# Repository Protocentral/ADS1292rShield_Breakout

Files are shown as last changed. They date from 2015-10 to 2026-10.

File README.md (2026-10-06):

ProtoCentral ADS1292R ECG/respiration shield and breakout board 
================================

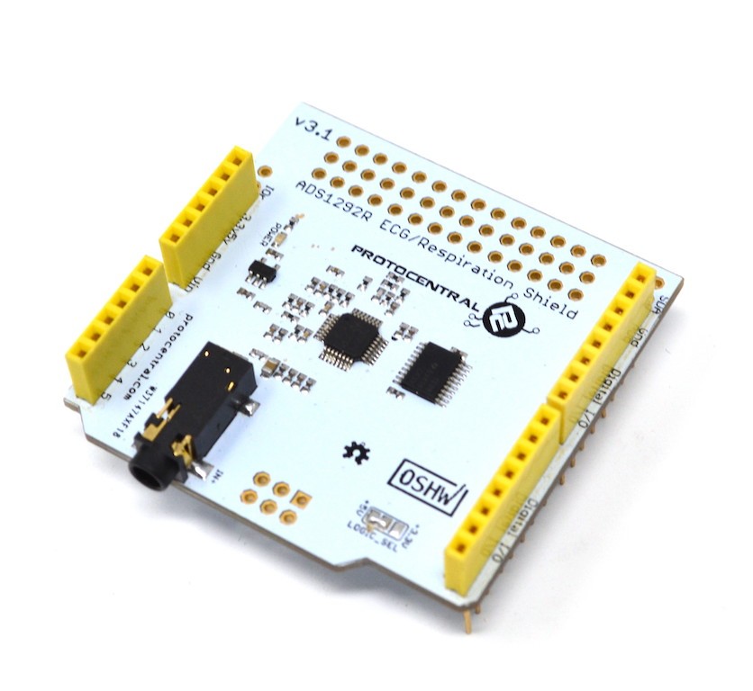
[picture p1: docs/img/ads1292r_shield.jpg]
ECG
[  
Dont have it yet? But one here: ADS1292R ECG/Respiration Shield for Arduino- v2 (PC-4128)](https://protocentral.com/product/ads1292r-ecg-respiration-shield-for-arduino-v2/)

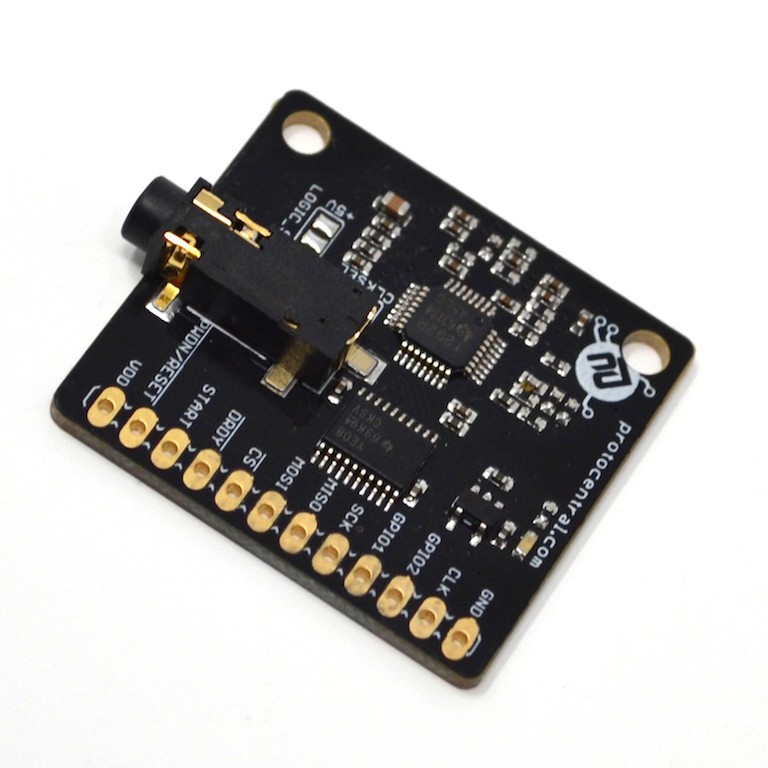
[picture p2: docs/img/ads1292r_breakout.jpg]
bob
[  
Dont have it yet? But one here: ADS1292R ECG/Respiration Breakout for Arduino- v3 (PC-4116)](https://protocentral.com/product/ads1292r-ecg-respiration-breakout-kit/)

The Arduino library for this product is now available in the **[ProtoCentral ADS1292R Arduino Library repo](https://github.com/Protocentral/protocentral-ads1292r-arduino)**

**Breakout v4:** KiCad design files and the schematic PDF are in [`hardware/breakout/v4`](hardware/breakout/v4). v4 has a new 10-pin host header (CS, MOSI, SCK, MISO, DRDY, START, RST, CLK, VCC, GND) with the ADS1292R clock brought out, so the pinout below applies to v3 only. Earlier revisions remain in `hardware/breakout` and `hardware/shield`.

Easily monitor ECG and respiration using your Arduino with this plug-in shield. The version 2 of this product adds a new SPI pin header making it compatible with newer Arduino devices including the Arduino Yun and 3.5mm connector for the electrodes. We now include the electrodes and cable also with the shield

Just plug it into an Arduino and you're ready to go. The 3.5 mm circular connector provides an easy way to connect electodes to the shield. The other end of this cable has snaps for standard ECG electrodes. We also include a pakc of 10 disposable EG electrodes. It accepts two ECG electrodes and one Driven Right Leg (DRL) electrode for common mode noise reduction. 

Another interesting feature of this shield is that you can also measure the respiratory activity using the same two electrodes connected to the shield. The ADS1292R uses a method known as impedance pneumography to measure respiration using the changes in chest impedance caused during respiration. 

Features:
----------
* ADS1292R Analog Front End IC
* Onboard 3.3V voltage regulator for low noise
* Onboard logic level transalators for Arduino interface
* Prototyping area for adding addtional components

Includes:
----------
* ADS1292R Arduino shield
* Electrode cable with 3.5mm connector and ECG electrodes connectors
* Pack of 10 disposable stick-on ECG electrodes.

Connecting the shield to your Arduino
-------------------------------------
Connect the ECG/Respiration shield to the Arduino by stacking it on top of your Arduino. This shield uses the SPI interface  to communicate with the Arduino. Since this includes the ICSP header, which is used on newer Arduinos for SPI communication,  this shield is also compatible newer Arduino boards such as the Arduino Yun and Due.
 
Wiring the Breakout to your Arduino
------------------------------------
 If you have bought the breakout the connection with the Arduino board is as follows:
 
|ads1292r pin label| Arduino Connection   |Pin Function      |
|----------------- |:--------------------:|-----------------:|
| VDD              | +5V                  |  Supply voltage  |             
| PWDN/RESET       | D4                   |  Reset           |
| START            | D5                   |  Start Input     |
| DRDY             | D6                   |  Data Ready Outpt|
| CS               | D7                   |  Chip Select     |
| MOSI             | D11                  |  Slave In        |
| MISO             | D12                  |  Slave Out       |
| SCK              | D13                  |  Serial Clock    |
| GND              | Gnd                  |  Gnd             |
 
Installing the Arduino libraries 
---------------------------------
Arduino library for this boards is now available at https://github.com/Protocentral/protocentral-ads1292r-arduino or from the Arduino Library Manager inside the Arduino IDe. 

If you have correctly installed the libraries, the example sketeches should now be available from within Arduino at File-->Examples-->ProtoCentral ADS1292R library.

Using the ProtoCentral OpenView GUI
-----------------------------------

The GUI for visualizing the ECG and Respiration as well as parameters like Heart rate and Respiration rate is written in Processing, based on Java and is cross-compilable across platforms. 
 
Java 8 is required on all platforms for running the processing-based GUI application. You can download Java for your platform from the [Official Java website](https://java.com/en/download/).

You can download and install [ProtoCentral OpenView](https://github.com/Protocentral/protocentral_openview) from here: https://github.com/Protocentral/protocentral_openview

Connecting the ECG Electrodes
------------------------------
 A 3-electrode cable along with a standard stereo jack is provided along with the shield to connect the electrodes to the     shield. The electrode input connector is highlighted in the below picture.
 
 The other side of the electrode connector would connect to snap-on electrodes attached to the body. For testing purposes,    you can use an ECG simulator to provide inputs to the board. 

 Warning:
 When connecting the electodes to the body, it is safer to disconnect the mains power source to the Arduino. For example, if  you are using the Arduino along with a laptop, disconnecting the battery charger from the laptop would be a safe option.
 
Placing the Electrodes on the body
---------------------------------
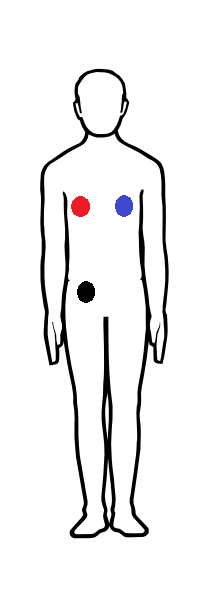
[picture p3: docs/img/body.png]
Wearing the Electrode


License Information
===================
This product is open source! 

OSHW Certified

Both, our hardware and software are open source and licensed under the following licenses:

License 

Hardware
---------

**All hardware is released under the [CERN-OHL-P v2](https://ohwr.org/cern_ohl_p_v2.txt)** license.

Copyright CERN 2020.

This source describes Open Hardware and is licensed under the CERN-OHL-P v2.

You may redistribute and modify this documentation and make products
using it under the terms of the CERN-OHL-P v2 (https:/cern.ch/cern-ohl).
This documentation is distributed WITHOUT ANY EXPRESS OR IMPLIED
WARRANTY, INCLUDING OF MERCHANTABILITY, SATISFACTORY QUALITY
AND FITNESS FOR A PARTICULAR PURPOSE. Please see the CERN-OHL-P v2
for applicable conditions

Software
--------

**All software is released under the MIT License(http://opensource.org/licenses/MIT).**

THE SOFTWARE IS PROVIDED "AS IS", WITHOUT WARRANTY OF ANY KIND, EXPRESS OR IMPLIED, INCLUDING BUT NOT LIMITED TO THE WARRANTIES OF MERCHANTABILITY, FITNESS FOR A PARTICULAR PURPOSE AND NONINFRINGEMENT. IN NO EVENT SHALL THE AUTHORS OR COPYRIGHT HOLDERS BE LIABLE FOR ANY CLAIM, DAMAGES OR OTHER LIABILITY, WHETHER IN AN ACTION OF CONTRACT, TORT OR OTHERWISE, ARISING FROM, OUT OF OR IN CONNECTION WITH THE SOFTWARE OR THE USE OR OTHER DEALINGS IN THE SOFTWARE.

Documentation
-------------
**All documentation is released under [Creative Commons Share-alike 4.0 International](http://creativecommons.org/licenses/by-sa/4.0/).**


You are free to:

* Share — copy and redistribute the material in any medium or format
* Adapt — remix, transform, and build upon the material for any purpose, even commercially.
The licensor cannot revoke these freedoms as long as you follow the license terms.

Under the following terms:

* Attribution — You must give appropriate credit, provide a link to the license, and indicate if changes were made. You may do so in any reasonable manner, but not in any way that suggests the licensor endorses you or your use.
* ShareAlike — If you remix, transform, or build upon the material, you must distribute your contributions under the same license as the original.

Please check [*LICENSE.md*](LICENSE.md) for detailed license descriptions.

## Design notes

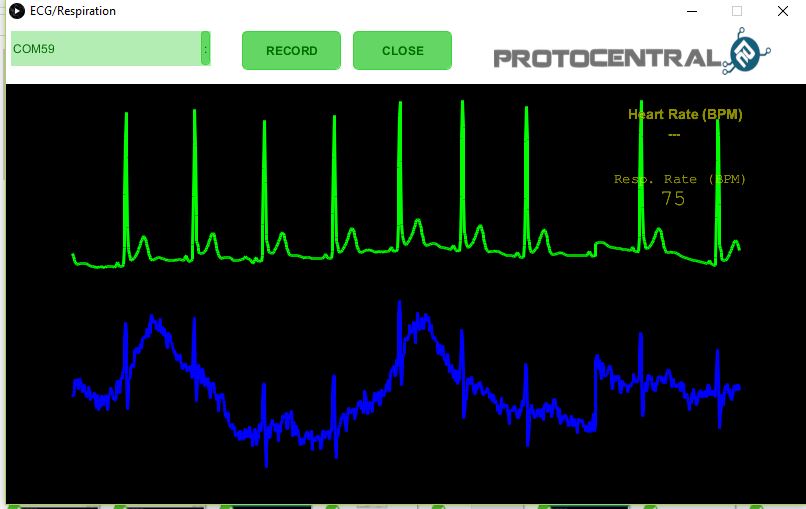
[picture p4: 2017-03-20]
docs/img/ads1292r_ecg_resp_screenshot.jpg

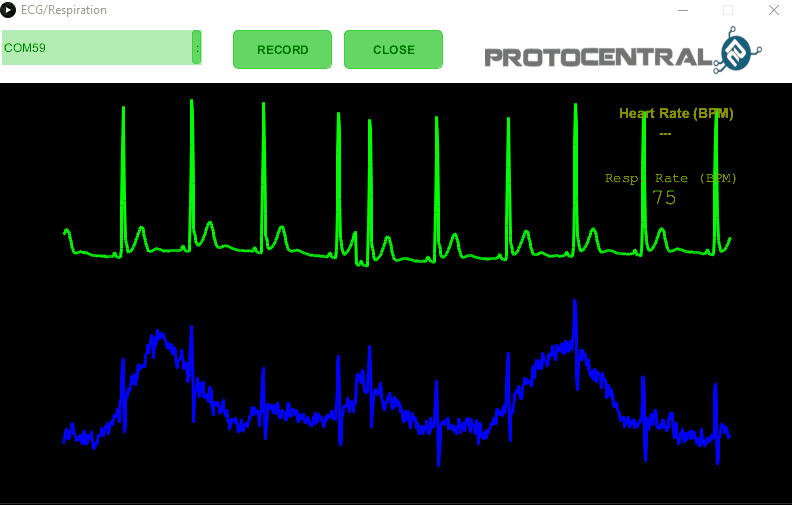
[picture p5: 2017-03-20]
docs/img/ecg_plot.gif

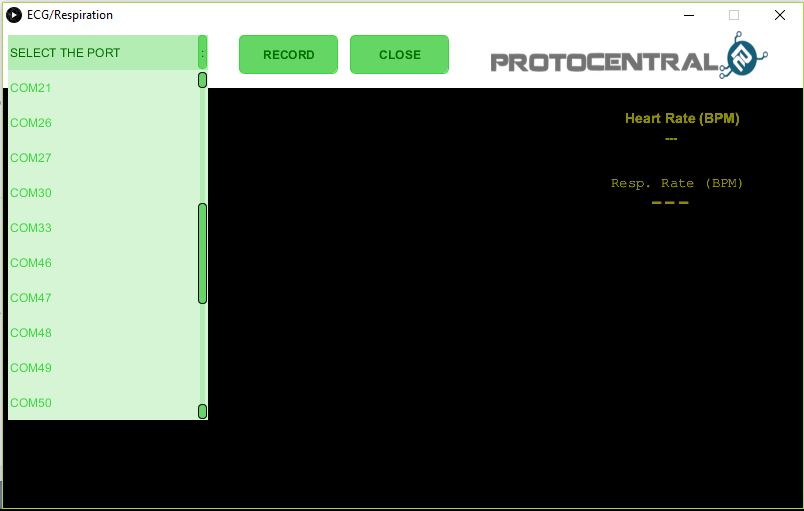
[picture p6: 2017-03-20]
docs/img/port_selection.JPG

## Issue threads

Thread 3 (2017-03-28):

Protocentral/ADS1292rShield_Breakout #3: bad results

ccarmielf, 2017-03-28:
i followed the steps laid out and im not getting any real results. It looks more like a beat (high and low frequency signal) then a pulse. any suggestion to what im doing wrong?

VenkateshBhat, 2017-03-29:
Hello ccarmielf,

1.  You did mention that you were facing some issues with the libraries, where did you get those instructions?
2.Recently we did update on gui and arduino sketch , could you please clone and try with the latest version
3.Please attach the obtained result.

ccarmielf, 2017-04-21:
Hi, So i got the right libraries added and the code uploads fine. Just my results are weird. 

[log.xlsx](https://github.com/Protocentral/ADS1292rShield_Breakout/files/948152/log.xlsx)

ccarmielf, 2017-04-21:
So here are the results with different lead placement.
[log.xlsx](https://github.com/Protocentral/ADS1292rShield_Breakout/files/948174/log.xlsx)

VenkateshBhat, 2017-04-24:
Hello,
The graph seems to be extremely erroneous, 

- are the electrodes placements are proper? 
- are you using shield or breakout?

preksha02, 2019-04-12:
hello VenkateshBhat 
can you help in finding the exact library for this.

yasaswinir, 2019-04-12:
Hello Preksha,
You can find the arduino library in the software/ folder of our github repo

preksha02, 2019-05-14:
https://photos.app.goo.gl/3jHZedEEafnVNs7H9
this is the link of my output. i dont get respiration rate, neither on arduino ide nor on processing

closed 2020-12-31 by protocentralashwin

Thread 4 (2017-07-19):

Protocentral/ADS1292rShield_Breakout #4: Never get DRDY

philgrim2, 2017-07-19:
Using the breakout board with an Uno R3.
Put in some Serial.println settings to try to discover why I don't get results.
DRDY never goes low.
I have two boards, same results with both.

VenkateshBhat, 2017-07-19:
Could you please attach the connection setup?

gcmike, 2017-09-29:
Same issue here. Any updates?

VenkateshBhat, 2017-09-29:
@gcmike 
Sorry for the inconvenience caused,
Please provide us the additional details/share the screenshots.

VenkateshBhat, 2017-09-30:
@gcmike thanks for sharing,
Couple of things:
- If your msp430xxx is 3.3V tolerable change the jumper setting on the breakout to 3.3V. By default it will be 5V.
- No additional pulldown is required since there is a on board level converter.
Ensure START and PWDN/RESET are pulled high.
[image]

closed 2020-12-31 by protocentralashwin

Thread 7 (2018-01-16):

Protocentral/ADS1292rShield_Breakout #7: Latest Version not showing any data on Windows 10

twhiting87, 2018-01-16:
Hi, Using the latest versions of Arduino and Processing code from Github (both compile and run correctly), the GUI screen is loading but, after choosing the correct COM port (4), there is no  data being passed through - see screen shot. I've checked the serial port using RealTerm and good data is coming through so the issue is somewhere in the Processing code. Any ideas?

[image]

kalineBr, 2018-01-16:
Maybe the serial.begin isn't synchronized: look at devices an printers->drivers->arduino->properties->serial.

shreythakker, 2018-06-08:
Facing the Same problem. was your issue resolved?

preksha02, 2019-05-14:
i am not able to compile processing code. Can you please send your processing code. @twhiting87

joicetm, 2019-05-14:
Hi,
Did you follow all procedure what we given in our official website(https://github.com/Protocentral/ADS1292rShield_Breakout),if you done those procedure please share the screenshot where you are getting error even though please share your order number.

preksha02, 2019-05-14:
Thankyou for replying!
https://photos.app.goo.gl/3jHZedEEafnVNs7H9
this is my output wave form.
i get the heart rate value, but not respiration rate value.
even though in arduino ide,i only get heart rate. there also a issue , the code i am using doesnt show values. here i am attaching my arduino ide output.
https://photos.google.com/photo/AF1QipNO8xMagkwqkP0eVKDIAztxl8fGNsTPNn8_oofC
my arduino program->
//////////////////////////////////////////////////////////////////////////////////////////
//
//   Arduino Library for ADS1292R Shield/Breakout
//
//   Copyright (c) 2017 ProtoCentral
//   Heartrate and respiration computation based on original code from Texas Instruments
//
//   This software is licensed under the MIT License(http://opensource.org/licenses/MIT).
//
//   THE SOFTWARE IS PROVIDED "AS IS", WITHOUT WARRANTY OF ANY KIND, EXPRESS OR IMPLIED, INCLUDING BUT
//   NOT LIMITED TO THE WARRANTIES OF MERCHANTABILITY, FITNESS FOR A PARTICULAR PURPOSE AND NONINFRINGEMENT.
//   IN NO EVENT SHALL THE AUTHORS OR COPYRIGHT HOLDERS BE LIABLE FOR ANY CLAIM, DAMAGES OR OTHER LIABILITY,
//   WHETHER IN AN ACTION OF CONTRACT, TORT OR OTHERWISE, ARISING FROM, OUT OF OR IN CONNECTION WITH THE
//   SOFTWARE OR THE USE OR OTHER DEALINGS IN THE SOFTWARE.
//
//   Requires g4p_control graphing library for processing.  Built on V4.1
//   Downloaded from Processing IDE Sketch->Import Library->Add Library->G4P Install

// If you have bought the breakout the connection with the Arduino board is as follows:
//
//|ads1292r pin label| Arduino Connection   |Pin Function      |
//|----------------- |:--------------------:|-----------------:|
//| VDD              | +5V                  |  Supply voltage  |
//| PWDN/RESET       | D4                   |  Reset           |
//| START            | D5                   |  Start Input     |
//| DRDY             | D6                   |  Data Ready Outpt|
//| CS               | D7                   |  Chip Select     |
//| MOSI             | D11                  |  Slave In        |
//| MISO             | D12                  |  Slave Out       |
//| SCK              | D13                  |  Serial Clock    |
//| GND              | Gnd                  |  Gnd             |
//
/////////////////////////////////////////////////////////////////////////////////////////

#include <ads1292r.h>
#include <SPI.h>

ads1292r ADS1292;   // define class

//Packet format
#define  CES_CMDIF_PKT_START_1      0x0A
#define  CES_CMDIF_PKT_START_2      0xFA
#define  CES_CMDIF_TYPE_DATA        0x02
#define  CES_CMDIF_PKT_STOP_1       0x00
#define  CES_CMDIF_PKT_STOP_2       0x0B

#define TEMPERATURE 0
#define FILTERORDER         161
/* DC Removal Numerator Coeff*/
#define NRCOEFF (0.992)
#define WAVE_SIZE  1

//******* ecg filter *********
#define MAX_PEAK_TO_SEARCH         5
#define MAXIMA_SEARCH_WINDOW      25
#define MINIMUM_SKIP_WINDOW       30
#define SAMPLING_RATE             125
#define TWO_SEC_SAMPLES           2 * SAMPLING_RATE
#define QRS_THRESHOLD_FRACTION    0.4
#define TRUE 1
#define FALSE 0

volatile uint8_t  SPI_Dummy_Buff[30];
[... 453 lines cut ...]
    {
      /* Reset heart rate computation sate variable in case of no peak found in 3 seconds */
      sample_count = 0 ;
      s_array_index = 0 ;
      m_array_index = 0 ;
      maxima_sum = 0 ;
      sample_index[0] = 0 ;
      sample_index[1] = 0 ;
      sample_index[2] = 0 ;
      sample_index[3] = 0 ;
      Start_Sample_Count_Flag = 0;
      peak_detected = FALSE ;
      sample_sum = 0;
      first_peak_detect = FALSE;
      nopeak = 0;
      QRS_Heart_Rate = 0;
    }
  }

  global_HeartRate = (uint8_t)QRS_Heart_Rate;
  //Serial.println(global_HeartRate);

}

kindly help!

joicetm, 2019-05-14:
please share your order number so that we can contact you directly to solve your issue

preksha02, 2019-05-14:
i am not getting it. what is order number? @joicetm

Mo7amed-Aazeem, 2019-10-07:
joicetm..
I have a problem with getting output from this circuit, after i following all of the mentioned steps,
can you help me please...
as fast as possible please

Email: Mo7amed99935@gmail.com 
Whatsapp: +249100100409

Mo7amed-Aazeem, 2019-10-08:
> please share your order number so that we can contact you directly to solve your issue

help me please...

MohammedHM, 2019-10-09:
Hello Aazeem,

Our ADS1292R Arduino library calculates heart rate, ECG waveform and Respiration waveform. We did not add respiration algorithm to calculate respiration value due to memory sufficiency while compiling in Arduino UNO. You can get the respiration algorithm from our [HealthyPi Arduino library ](https://github.com/Protocentral/protocentral-healthypi-v3/blob/master/firmware/healthypi3_streaming/healthypi3_streaming.ino) and you can add this algorithm and try with some boards with more memory like Arduino mega.

MohammedHM, 2019-10-09:
Hello Aazeem,

Please share the screenshots of your GUI and the error your facing to get output. Surely we can help you in figuring it out.

Mo7amed-Aazeem, 2019-10-09:
Thank you for replying… I'm trying to implement a system to measure ECG signal + respiration + heartrate..so I chose to work with your ads1292r, I follow all of the steps that mentioned in the site,  but I have no output at all,  some times the output come-out as a very noisy signal (I will send you a screenshot for it) and sometimes there is no output but the noisy signal appears with body movement and disappear again. But usually there is no response…Actually I was read about the module and the project before getting it,  so I decide to use the arduino due,  in stead of uno because of the better specifications of it(memory,  speed and so on) Sent from my Huawei Mobile-------- Original Message --------Subject: Re: [Protocentral/ADS1292rShield_Breakout] Latest Version not showing any data on Windows 10 (#7)From: Mohammed Ibrahim To: Protocentral/ADS1292rShield_Breakout CC: Mo7amed-Aazeem ,Comment Hello Aazeem,
Our ADS1292R Arduino library calculates heart rate, ECG waveform and Respiration waveform. We did not add respiration algorithm to calculate respiration value due to memory sufficiency while compiling in Arduino UNO. You can get the respiration algorithm from our HealthyPi Arduino library  and you can add this algorithm and try with some boards with more memory like Arduino mega.

Mo7amed-Aazeem, 2019-10-09:
Sent from my Huawei Mobile-------- Original Message --------Subject: Re: [Protocentral/ADS1292rShield_Breakout] Latest Version not showing any data on Windows 10 (#7)From: Mohammed Ibrahim To: Protocentral/ADS1292rShield_Breakout CC: Mo7amed-Aazeem ,Comment Hello Aazeem,
Our ADS1292R Arduino library calculates heart rate, ECG waveform and Respiration waveform. We did not add respiration algorithm to calculate respiration value due to memory sufficiency while compiling in Arduino UNO. You can get the respiration algorithm from our HealthyPi Arduino library  and you can add this algorithm and try with some boards with more memory like Arduino mega.

closed 2020-12-31 by protocentralashwin

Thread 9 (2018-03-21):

Protocentral/ADS1292rShield_Breakout #9: global_respirationRate is null

kaline, 2018-03-21:
Inside the example code is not possible measure the respiration, the monitor serial always print '0':
Somebody has any ideas about the problem?

The piece of code:

  Serial.print("heart_rate->");
  Serial.println(global_HeartRate);
  Serial.print("respiration_rate-> ");
  Serial.println(global_RespirationRate);

pzink, 2018-11-23:
The most recent example code doesn't include any output of respiration rate. Is there older or better example code that includes that?

yasaswinir, 2018-11-24:
Hello @pzink @kaline , 
Sorry for the inconvenience. We are trying to fix the issues in both GUI and the code. Meanwhile if you want to check the respiration rate , you can verify in the log file created after you click record in the Processing GUI. The respiration rate is saved into the log file.

Thank you for bringing the issue forward!

preksha02, 2019-05-14:
@yasaswinir 
whether the issue resolve? because still i am facing the same problem. I am only able to view ECG not the respiration in arduino IDE.

yingshaoxo, 2020-10-04:
whether the issue resolve? because still i am facing the same problem. I am only able to view ECG not the respiration in arduino IDE.

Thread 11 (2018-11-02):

Protocentral/ADS1292rShield_Breakout #11: ECG lead error!!! ensure the leads are properly connected

davidm-public, 2018-11-02:
Hi, uploaded the `text_only' arduino file, got the following:

```
Initiliziation is done
ECG lead error!!! ensure the leads are properly connected
ECG lead error!!! ensure the leads are properly connected
ECG lead error!!! ensure the leads are properly connected
etc.
```

thing is that I've placed thousands of ecg electrodes in my time, and I can honestly say that these leads are indeed connected !

yasaswinir, 2018-11-05:
Hello David sir! Glad you could figure out the issue! Thank you so much for your acknowledgment! Please do let us know if we could be of any further service to you!

davidm-public, 2018-11-18:
Hi there, looks like your website is down.
I'd like to order a few more of those boards.

David

closed 2018-11-18 by davidm-public

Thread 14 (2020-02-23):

Protocentral/ADS1292rShield_Breakout #14: Error while Compiling

shabir67, 2020-02-23:
Just get the package recently any body knows hot to deal with this error message ??
Arduino: 1.8.5 (Windows 10), Board: "Arduino Uno"

> D:\Arduino\arduino-builder -dump-prefs -logger=machine -hardware D:\Arduino\hardware -hardware D:\Arduino\portable\packages -tools D:\Arduino\tools-builder -tools D:\Arduino\hardware\tools\avr -tools D:\Arduino\portable\packages -built-in-libraries D:\Arduino\libraries -libraries D:\Arduino\portable\sketchbook\libraries -fqbn=arduino:avr:uno -ide-version=10805 -build-path C:\Users\SHABIR~1\AppData\Local\Temp\arduino_build_774088 -warnings=none -build-cache C:\Users\SHABIR~1\AppData\Local\Temp\arduino_cache_153723 -prefs=build.warn_data_percentage=75 -prefs=runtime.tools.avr-gcc.path=D:\Arduino\portable\packages\arduino\tools\avr-gcc\7.3.0-atmel3.6.1-arduino5 -prefs=runtime.tools.avrdude.path=D:\Arduino\portable\packages\arduino\tools\avrdude\6.3.0-arduino17 -prefs=runtime.tools.arduinoOTA.path=D:\Arduino\portable\packages\arduino\tools\arduinoOTA\1.3.0 -verbose C:\Users\Shabir As\Desktop\TA\Proto Central\Protocentral_ADS1292R\examples\ECG-Respiration-Plot\ECG-Respiration-Plot.ino
> D:\Arduino\arduino-builder -compile -logger=machine -hardware D:\Arduino\hardware -hardware D:\Arduino\portable\packages -tools D:\Arduino\tools-builder -tools D:\Arduino\hardware\tools\avr -tools D:\Arduino\portable\packages -built-in-libraries D:\Arduino\libraries -libraries D:\Arduino\portable\sketchbook\libraries -fqbn=arduino:avr:uno -ide-version=10805 -build-path C:\Users\SHABIR~1\AppData\Local\Temp\arduino_build_774088 -warnings=none -build-cache C:\Users\SHABIR~1\AppData\Local\Temp\arduino_cache_153723 -prefs=build.warn_data_percentage=75 -prefs=runtime.tools.avr-gcc.path=D:\Arduino\portable\packages\arduino\tools\avr-gcc\7.3.0-atmel3.6.1-arduino5 -prefs=runtime.tools.avrdude.path=D:\Arduino\portable\packages\arduino\tools\avrdude\6.3.0-arduino17 -prefs=runtime.tools.arduinoOTA.path=D:\Arduino\portable\packages\arduino\tools\arduinoOTA\1.3.0 -verbose C:\Users\Shabir As\Desktop\TA\Proto Central\Protocentral_ADS1292R\examples\ECG-Respiration-Plot\ECG-Respiration-Plot.ino
> Using board 'uno' from platform in folder: D:\Arduino\portable\packages\arduino\hardware\avr\1.8.2
> Using core 'arduino' from platform in folder: D:\Arduino\portable\packages\arduino\hardware\avr\1.8.2
> Detecting libraries used...
> "D:\Arduino\portable\packages\arduino\tools\avr-gcc\7.3.0-atmel3.6.1-arduino5/bin/avr-g++" -c -g -Os -w -std=gnu++11 -fpermissive -fno-exceptions -ffunction-sections -fdata-sections -fno-threadsafe-statics -Wno-error=narrowing  -flto -w -x c++ -E -CC -mmcu=atmega328p -DF_CPU=16000000L -DARDUINO=10805 -DARDUINO_AVR_UNO -DARDUINO_ARCH_AVR   "-ID:\Arduino\portable\packages\arduino\hardware\avr\1.8.2\cores\arduino" "-ID:\Arduino\portable\packages\arduino\hardware\avr\1.8.2\variants\standard" "C:\Users\SHABIR~1\AppData\Local\Temp\arduino_build_774088\sketch\ECG-Respiration-Plot.ino.cpp" -o "nul"
> "D:\Arduino\portable\packages\arduino\tools\avr-gcc\7.3.0-atmel3.6.1-arduino5/bin/avr-g++" -c -g -Os -w -std=gnu++11 -fpermissive -fno-exceptions -ffunction-sections -fdata-sections -fno-threadsafe-statics -Wno-error=narrowing  -flto -w -x c++ -E -CC -mmcu=atmega328p -DF_CPU=16000000L -DARDUINO=10805 -DARDUINO_AVR_UNO -DARDUINO_ARCH_AVR   "-ID:\Arduino\portable\packages\arduino\hardware\avr\1.8.2\cores\arduino" "-ID:\Arduino\portable\packages\arduino\hardware\avr\1.8.2\variants\standard" "C:\Users\SHABIR~1\AppData\Local\Temp\arduino_build_774088\sketch\ECG-Respiration-Plot.ino.cpp" -o "C:\Users\SHABIR~1\AppData\Local\Temp\arduino_build_774088\preproc\ctags_target_for_gcc_minus_e.cpp"
> C:\Users\Shabir As\Desktop\TA\Proto Central\Protocentral_ADS1292R\examples\ECG-Respiration-Plot\ECG-Respiration-Plot.ino:20:10: fatal error: ads1292r.h: No such file or directory
> 
>  #include <ads1292r.h>
> 
>           ^~~~~~~~~~~~
> 
> compilation terminated.
> 
> exit status 1
> Error compiling for board Arduino Uno.

MarijnStam, 2020-02-24:
You have to include the library in your Arduino enviroment.

Sketch -> Include Library -> Add .ZIP library 
and then select the libraries which you can download [here](https://github.com/Protocentral/ADS1292rShield_Breakout/releases/download/v1.0/Protocentral_ADS1292R-v1.0-arduino.zip)

shabir67, 2020-03-12:
Thank you very much.One more question, is it possible to send this data package to and MySQL DB with esp8266 module ??.

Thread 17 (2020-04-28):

Protocentral/ADS1292rShield_Breakout #17: Read the respiration data to Arduino serial console.

desertwire, 2020-04-28:
Is there any way to read the value of the respiration and heart rate without using the Protocentral GUI. Printing DataPacketHeader to the console just results in corrupted ASCII.

```C
DataPacketHeader[9] = s32DaqVals[0];            // 4 bytes Respiration data
DataPacketHeader[10] = s32DaqVals[0]>>8;
DataPacketHeader[11] = s32DaqVals[0]>>16;
DataPacketHeader[12] = s32DaqVals[0]>>24; 

    for(i=0; i<15; i++) 
    {
      Serial.write(i);
      Serial.write(DataPacketHeader[i]);     // transmit the data over USB
    } 
```

Here is the output below of the Arduino serial monitor, is there any way to make sense of the data or how it is converted to a readable integer on the GUI?

```
⸮ < 0 p s | ` r I @ @ 9   	⸮ ⸮ ⸮ ⸮ ⸮ ⸮ ⸮ ⸮ ⸮ ⸮ ⸮ ⸮ < 2 $ & O ` q ` 8 0 ! > ⸮ ⸮ ⸮ ⸮ ⸮  ! 8 ! | H a @  9 $  ! ⸮ 8 B x  ⸮ ⸮ ⸮ ⸮  y a ` p 	f ⸮ ⸮ ⸮ ⸮ ⸮ 1 b N p ⸮ ⸮ ⸮ ⸮ ⸮ ⸮ ⸮ ⸮ " D ` ` ` p  
 ! ⸮ ⸮ ⸮ ⸮ ⸮ ⸮ ⸮ ⸮ ⸮ ⸮ ⸮ ⸮ ⸮ ⸮ ⸮ ⸮ 0 ⸮ ' # 3 @ O ` D B @ @ ! ⸮ ⸮ ⸮ ⸮ ⸮ 0 	a F ⸮ ⸮ ⸮ ⸮ ⸮ ⸮ " x p $ 0 ⸮ ⸮ ⸮ ⸮ ⸮ ⸮ ⸮ ⸮ ? q ` c x L b 8 9 $ 	⸮ ⸮ ⸮ ⸮ ⸮ ⸮ ⸮ ⸮ ⸮ ⸮ ⸮ 0 " ' & ⸮ & 8 # s ` a f H @ p | c N ~ "  ⸮ ⸮ ⸮ ⸮ ⸮ ⸮ ⸮ ⸮ @ D O D " ⸮ ⸮ ⸮ ⸮ ⸮ ⸮ ⸮ ⸮ ⸮ ⸮ $  F @ p 0 2 ⸮ ⸮ 
```

desertwire, 2020-04-28:
[Link](https://arduino.stackexchange.com/questions/75216/read-the-respiration-data-to-arduino-serial-console) to discussion.

protocentralashwin, 2020-12-31:
From the previous comment by @ryanjonesxyz, this will be in the format as required by [ProtoCentral OpenView](https://github.com/Protocentral/protocentral_openview)

closed 2020-12-31 by protocentralashwin

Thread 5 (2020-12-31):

### ISSUE TITLE
Using Raspberry Pi 3

### ISSUE THREAD

**Issue by meerasubramanian** [Protocentral/ADS1292rShield_Breakout#5]
I would like to connect the AFE _directly_ to Raspberry Pi without an Arduino.
I planned on using only the MISO, MOSI, CS(0), SCL pins from both AFE and RasPi.
Please guide me on the changes i need to make in the processing code so as to take input from the GPIO pins and plot it in Processing.

**Comment by shreythakker** [comment]
Did you figure it out or find some library that helps with interfacing the pi with the breakout board?

**Comment by shanmukhnama** [comment]
Is there some way of doing so by using the spidev library?

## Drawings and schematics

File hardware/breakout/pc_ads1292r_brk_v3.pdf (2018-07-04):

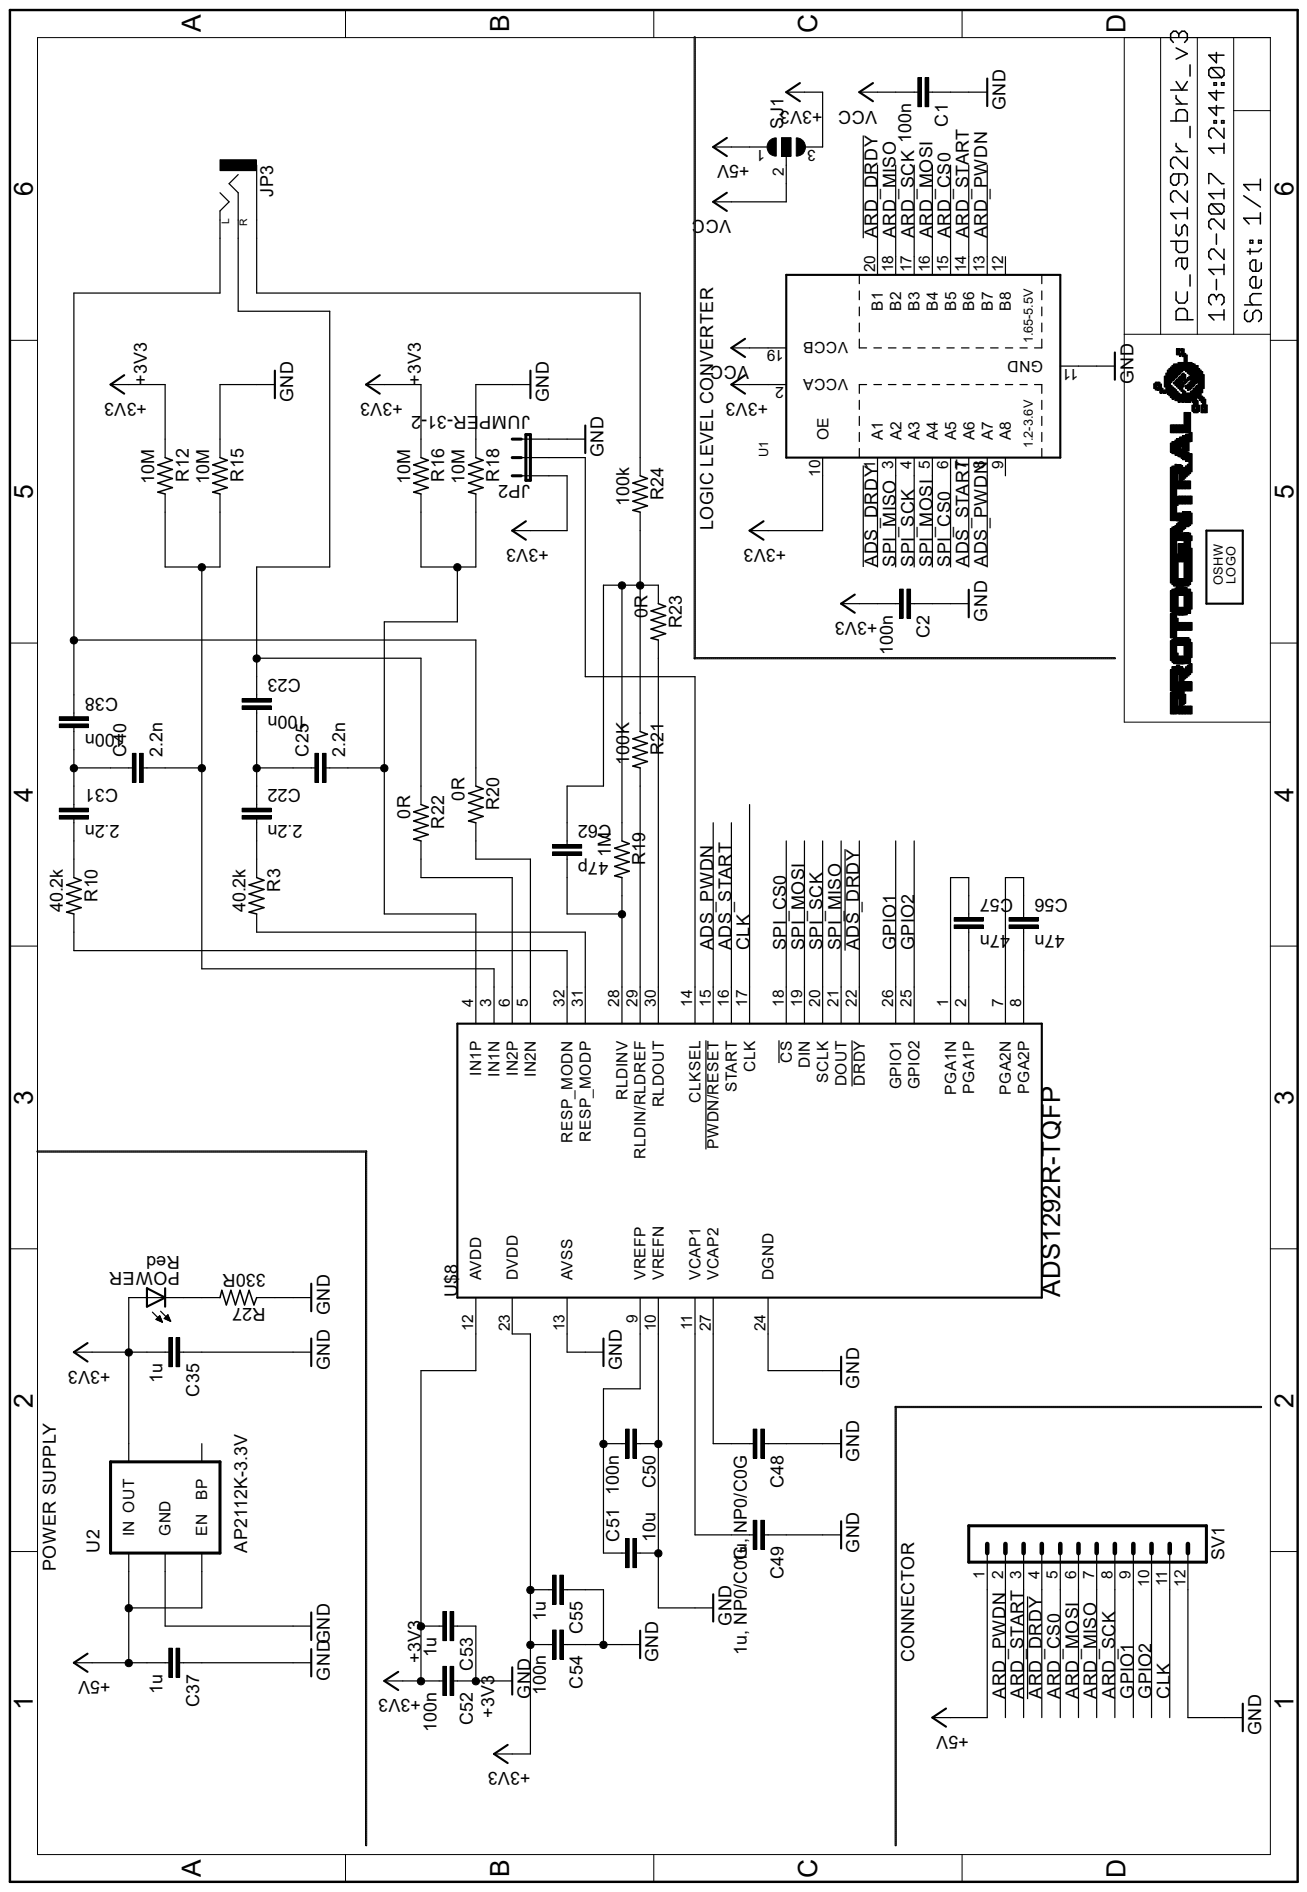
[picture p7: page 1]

2 U2INGNDOUT EN BP ADS_DRDY ADS_DRDY SPI_MISO SPI_MISO SPI_SCK SPI_SCK SPI_MOSI SPI_MOSI SPI_CS0 SPI_CS0 ADS_PWDN ADS_PWDN ADS_START ADS_START +3V3 +3V3 +3V3 +3V3 ARD_MOSI ARD_MOSI ARD_MISO ARD_MISO ARD_SCK ARD_SCK ARD_CS0 ARD_CS0 ARD_DRDY ARD_DRDY ARD_START ARD_START ARD_PWDN ARD_PWDN CLK CLK GPIO1 GPIO1 GPIO2 GPIO2

4 DIN 19 DOUT 21 SCLK 20 CS 18 DRDY 22 AVDD 12 AVSS 13 DVDD 23 GPIO1 26 GPIO2 25 RLDINV 28 RLDIN/RLDREF 29 RLDOUT 30 VREFP

9 VREFN 10 VCAP1 11 VCAP2 27 DGND 24 RESP_MODN 32 RESP_MODP 31 PWDN/RESET 15 CLK 17 START 16 CLKSEL 14 PGA1N

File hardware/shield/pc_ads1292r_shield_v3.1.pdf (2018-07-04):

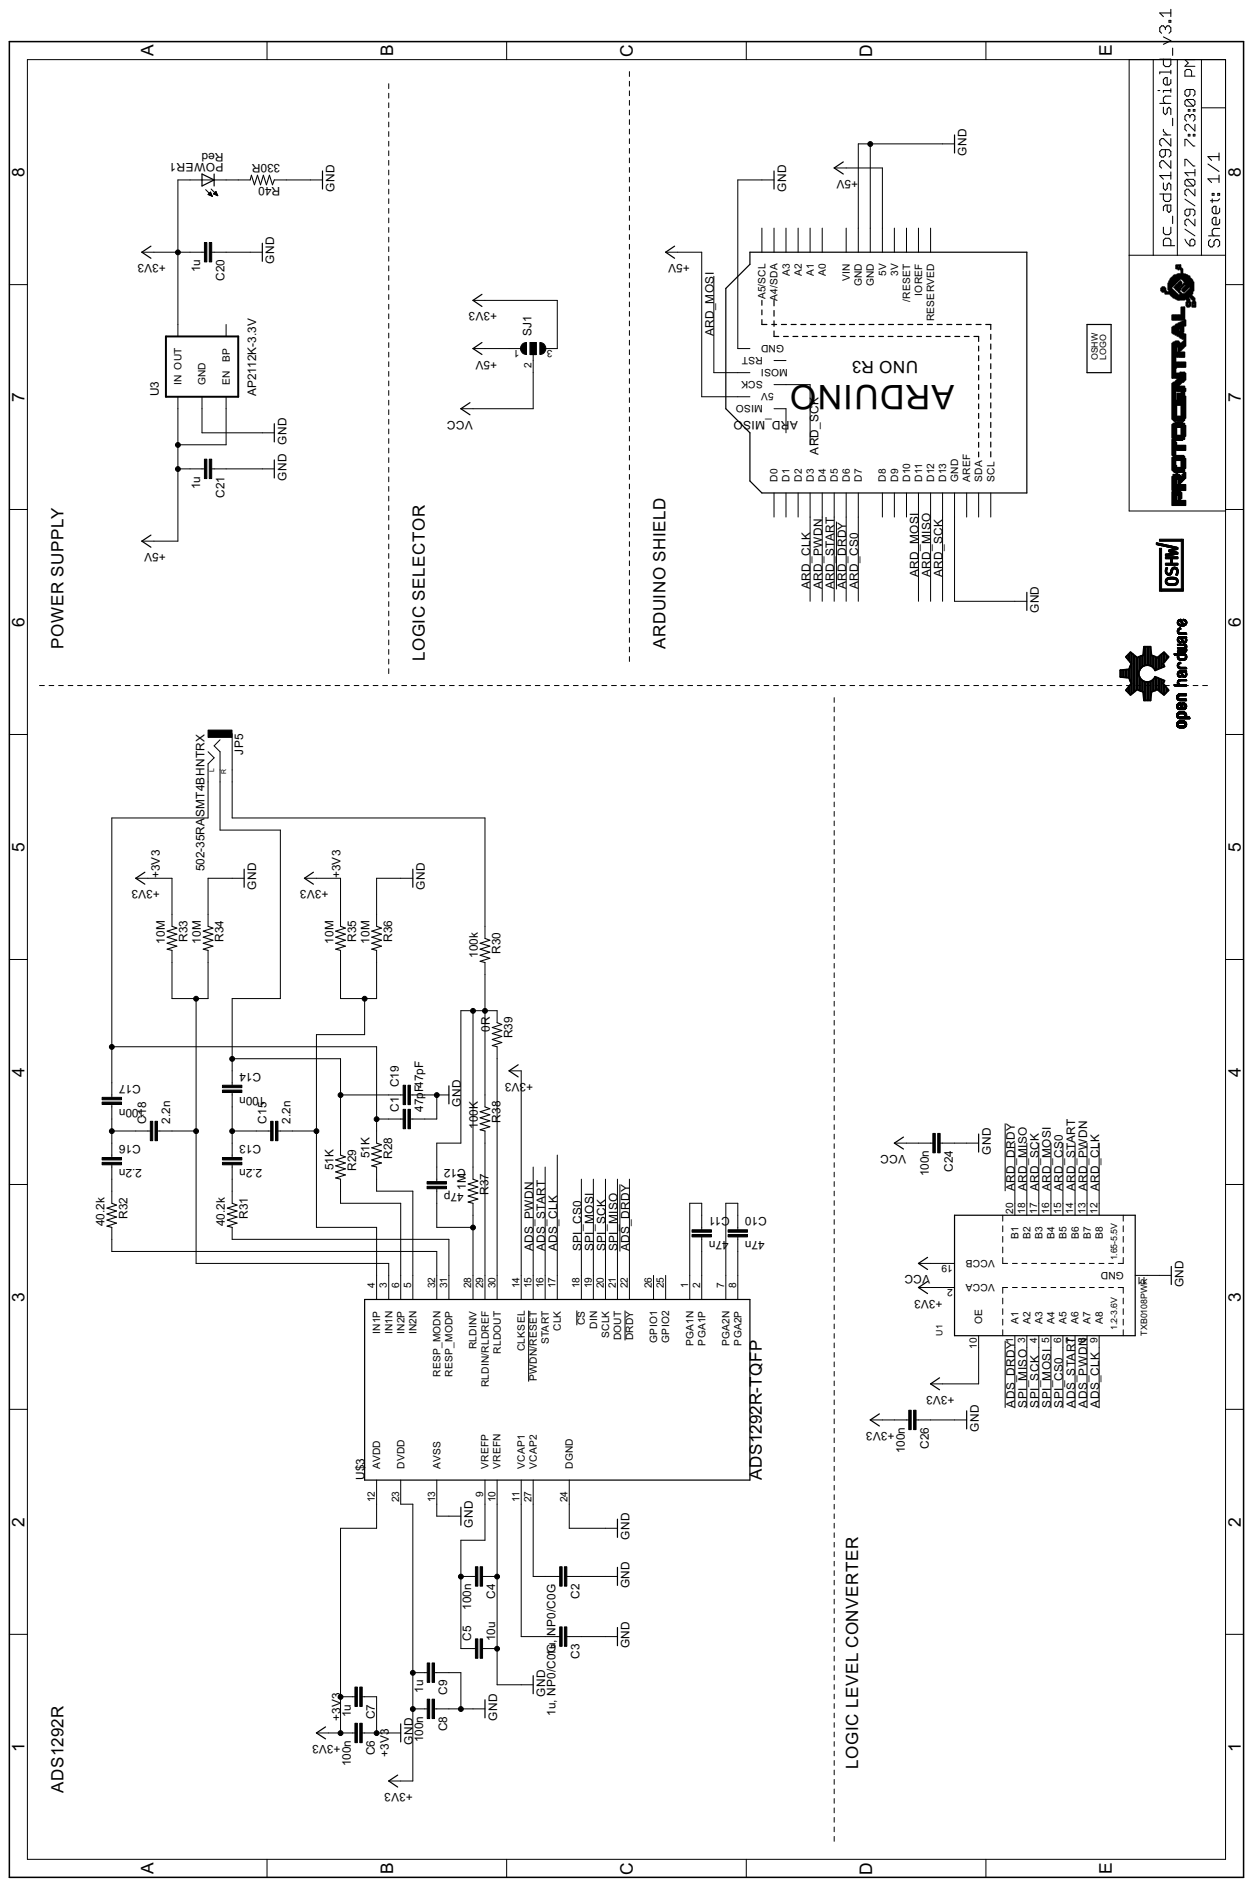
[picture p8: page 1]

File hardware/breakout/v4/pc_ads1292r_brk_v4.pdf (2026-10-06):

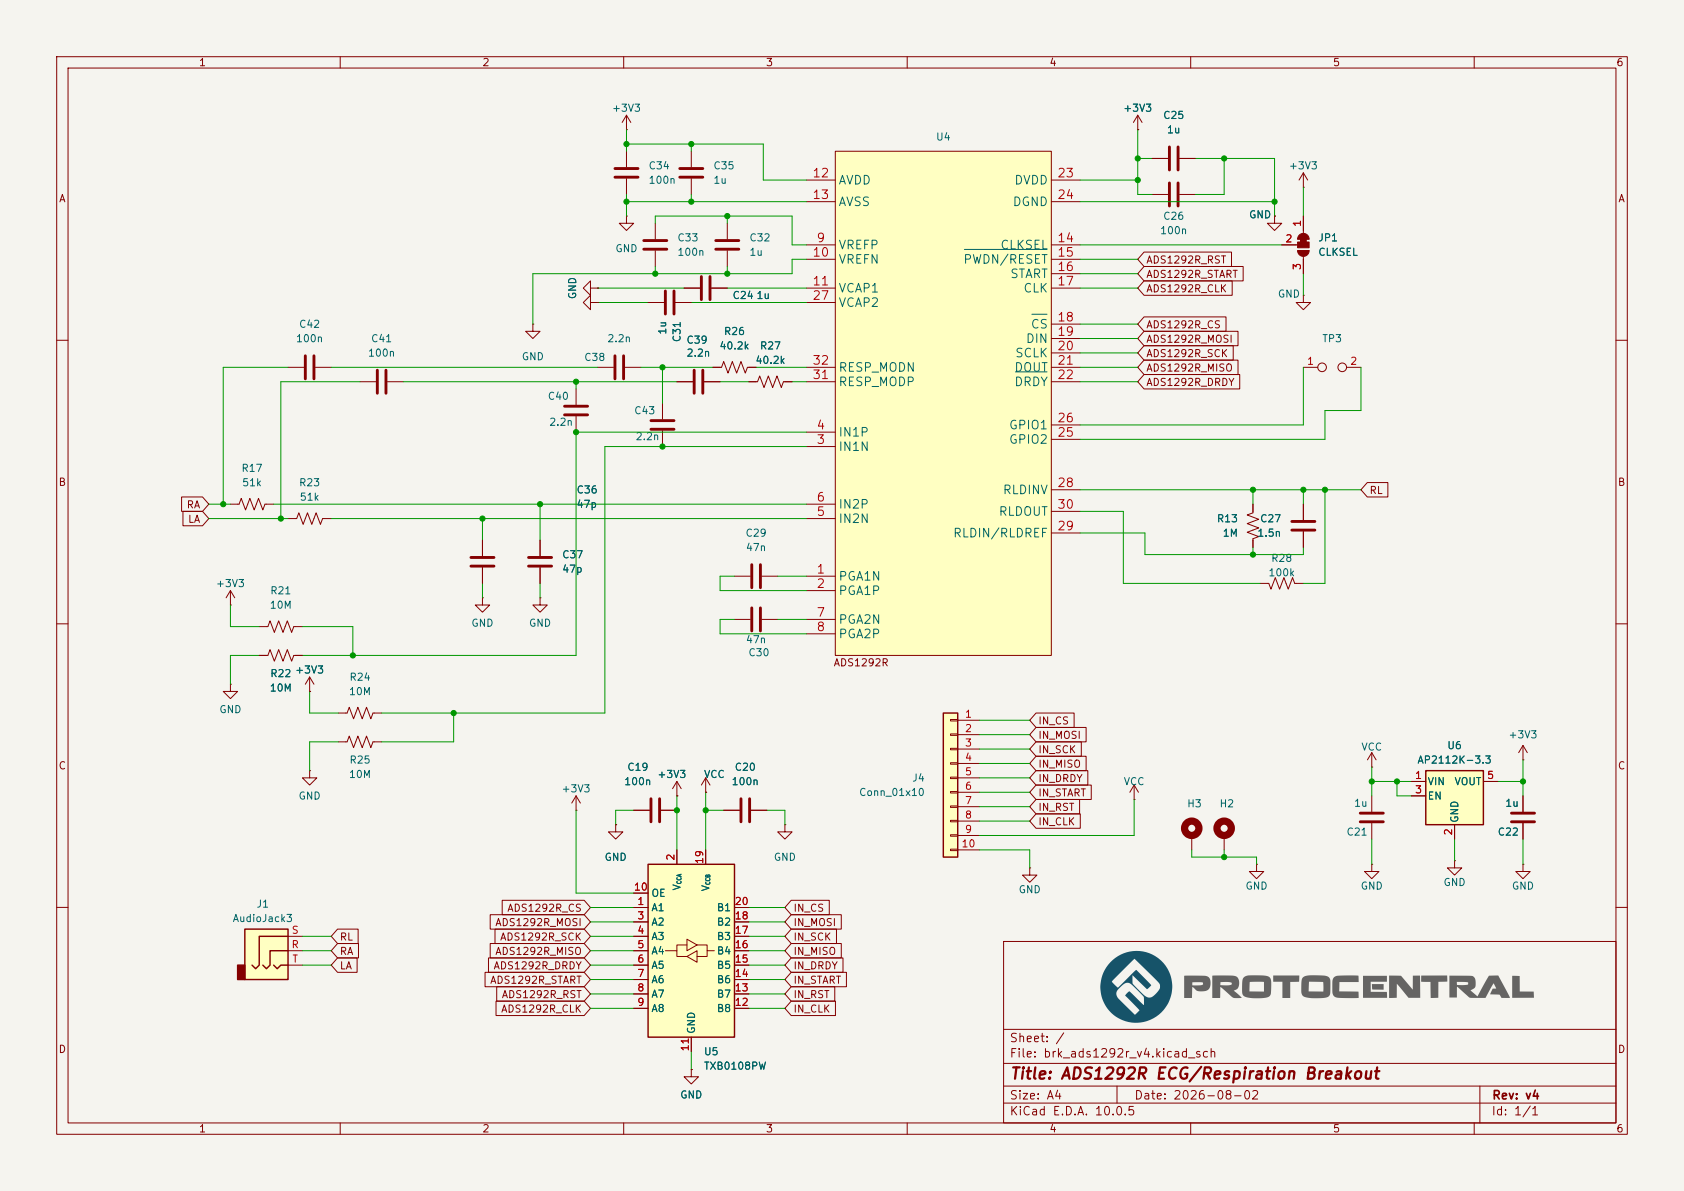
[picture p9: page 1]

Sheet: /
File: brk_ads1292r_v4.kicad_sch
Title: ADS1292R ECG/Respiration Breakout

Size: A4 | Rev: v4
KiCad E.D.A. 10.0.5 | Id: 1/1

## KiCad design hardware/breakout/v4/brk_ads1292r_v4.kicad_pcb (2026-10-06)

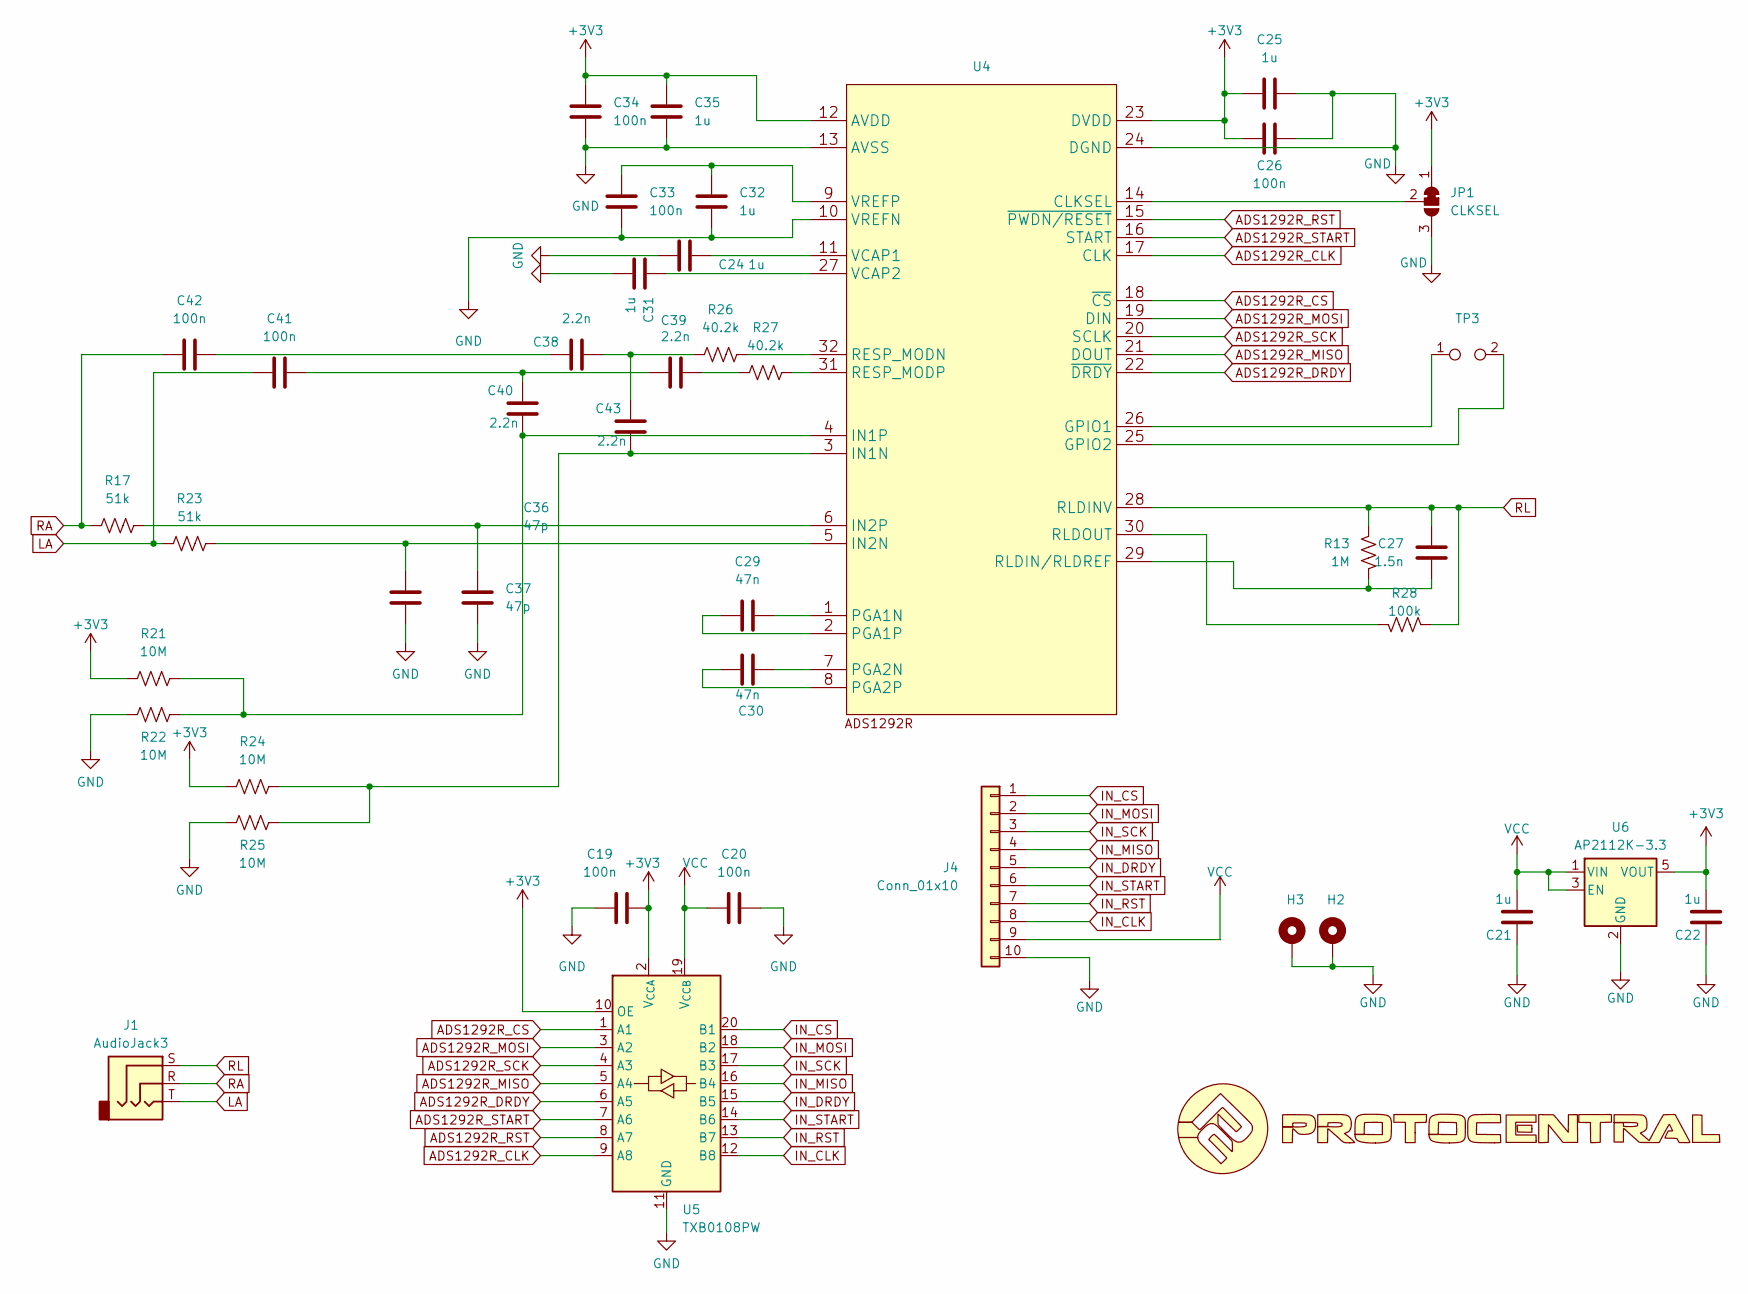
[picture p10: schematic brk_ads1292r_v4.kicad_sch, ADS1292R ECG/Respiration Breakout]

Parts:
C19, C20, C26, C33, C34, C41, C42: 100n; C_0402_1005Metric
C21, C22, C24, C25, C31, C32, C35: 1u; C_0402_1005Metric
C27: 1.5n; C_0402_1005Metric
C29, C30: 47n; C_0402_1005Metric
C36, C37: 47p; C_0402_1005Metric
C38, C39, C40, C43: 2.2n; C_0402_1005Metric
H2, H3: MountingHole_Pad; MountingHole_2.2mm_M2_DIN965_Pad_TopBottom
J1: AudioJack3; Jack_3.5mm_CUI_SJ-3523-SMT_Horizontal
J4: Conn_01x10; PinSocket_1x10_P2.54mm_Vertical
JP1: CLKSEL; SolderJumper-3_P1.3mm_Bridged2Bar12_RoundedPad1.0x1.5mm
R13: 1M; R_0402_1005Metric
R17, R23: 51k; R_0402_1005Metric
R21, R22, R24, R25: 10M; R_0402_1005Metric
R26, R27: 40.2k; R_0402_1005Metric
R28: 100k; R_0402_1005Metric
TP3: TestPoint_2Pole; TestPoint_2Pads_Pitch2.54mm_Drill0.8mm
U1: LOGO
U4: ADS1292R; PBS32
U5: TXB0108PW; TSSOP-20_4.4x6.5mm_P0.65mm
U6: AP2112K-3.3; SOT-23-5

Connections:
+3V3: C19.1, C22.2, C25.2, C26.2, C34.1, C35.1, JP1.1 (A), R21.1, R24.1, U4.12 (AVDD), U4.23 (DVDD), U5.2 (V_{CCA}), U5.10 (OE), U6.5 (VOUT)
ADS1292R_CLK: U4.17 (CLK), U5.9 (A8)
ADS1292R_CS: U4.18 (~CS), U5.1 (A1)
ADS1292R_DRDY: U4.22 (~DRDY), U5.6 (A5)
ADS1292R_MISO: U4.21 (DOUT), U5.5 (A4)
ADS1292R_MOSI: U4.19 (DIN), U5.3 (A2)
ADS1292R_RST: U4.15 (~PWDN/RESET), U5.8 (A7)
ADS1292R_SCK: U4.20 (SCLK), U5.4 (A3)
ADS1292R_START: U4.16 (START), U5.7 (A6)
GND: C19.2, C20.2, C21.1, C22.1, C24.2, C25.1, C26.1, C31.1, C32.2, C33.2, C34.2, C35.2, C36.2, C37.2, H2.1 (1_1), H3.1 (1_1), J4.10, JP1.3 (B), R22.1, R25.1, U4.10 (VREFN), U4.13 (AVSS), U4.24 (DGND), U5.11 (GND), U6.2 (GND)
IN_CLK: J4.8, U5.12 (B8)
IN_CS: J4.1, U5.20 (B1)
IN_DRDY: J4.5, U5.15 (B5)
IN_MISO: J4.4, U5.16 (B4)
IN_MOSI: J4.2, U5.18 (B2)
IN_RST: J4.7, U5.13 (B7)
IN_SCK: J4.3, U5.17 (B3)
IN_START: J4.6, U5.14 (B6)
LA: C41.2, J1.T, R23.1
unnamed: C38.1, C43.1, R26.1
unnamed: C38.2, C42.1
unnamed: C39.1, R27.1
unnamed: C39.2, C40.1, C41.1
unnamed: JP1.2 (C), U4.14 (CLKSEL)
unnamed: TP3.1, U4.26 (GPIO1)
unnamed: TP3.2, U4.25 (GPIO2)
unnamed: C43.2, R24.2, R25.2, U4.3 (IN1N)
unnamed: C40.2, R21.2, R22.2, U4.4 (IN1P)
unnamed: C36.1, R23.2, U4.5 (IN2N)
unnamed: C37.1, R17.2, U4.6 (IN2P)
unnamed: C29.1, U4.1 (PGA1N)
unnamed: C29.2, U4.2 (PGA1P)
unnamed: C30.1, U4.7 (PGA2N)
unnamed: C30.2, U4.8 (PGA2P)
unnamed: R26.2, U4.32 (RESP_MODN)
unnamed: R27.2, U4.31 (RESP_MODP)
unnamed: C27.1, R13.2, U4.29 (RLDIN/RLDREF)
unnamed: R28.2, U4.30 (RLDOUT)
unnamed: C24.1, U4.11 (VCAP1)
unnamed: C31.2, U4.27 (VCAP2)
unnamed: C32.1, C33.1, U4.9 (VREFP)
RA: C42.2, J1.R, R17.1
RL: C27.2, J1.S, R13.1, R28.1, U4.28 (RLDINV)
VCC: C20.1, C21.2, J4.9, U5.19 (V_{CCB}), U6.1 (VIN), U6.3 (EN)

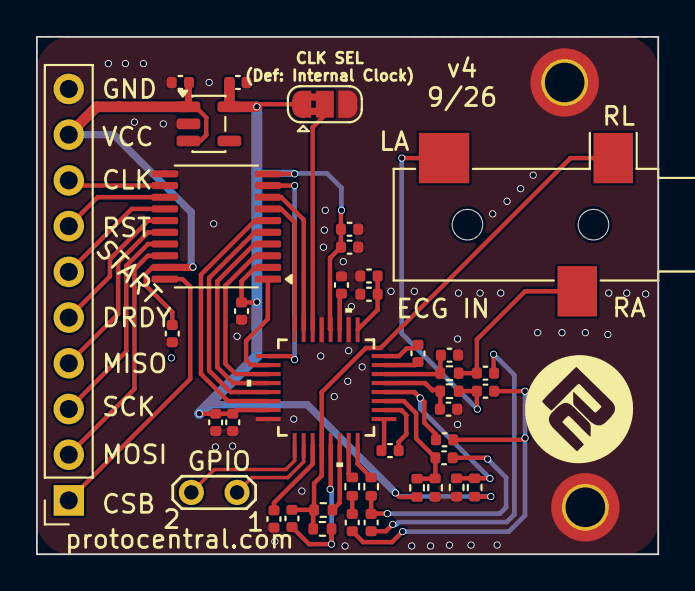
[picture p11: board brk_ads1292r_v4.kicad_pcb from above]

Board: 2 copper layers, 34.5 x 28.7 mm, 42 parts (0 on the bottom side), 44 nets.

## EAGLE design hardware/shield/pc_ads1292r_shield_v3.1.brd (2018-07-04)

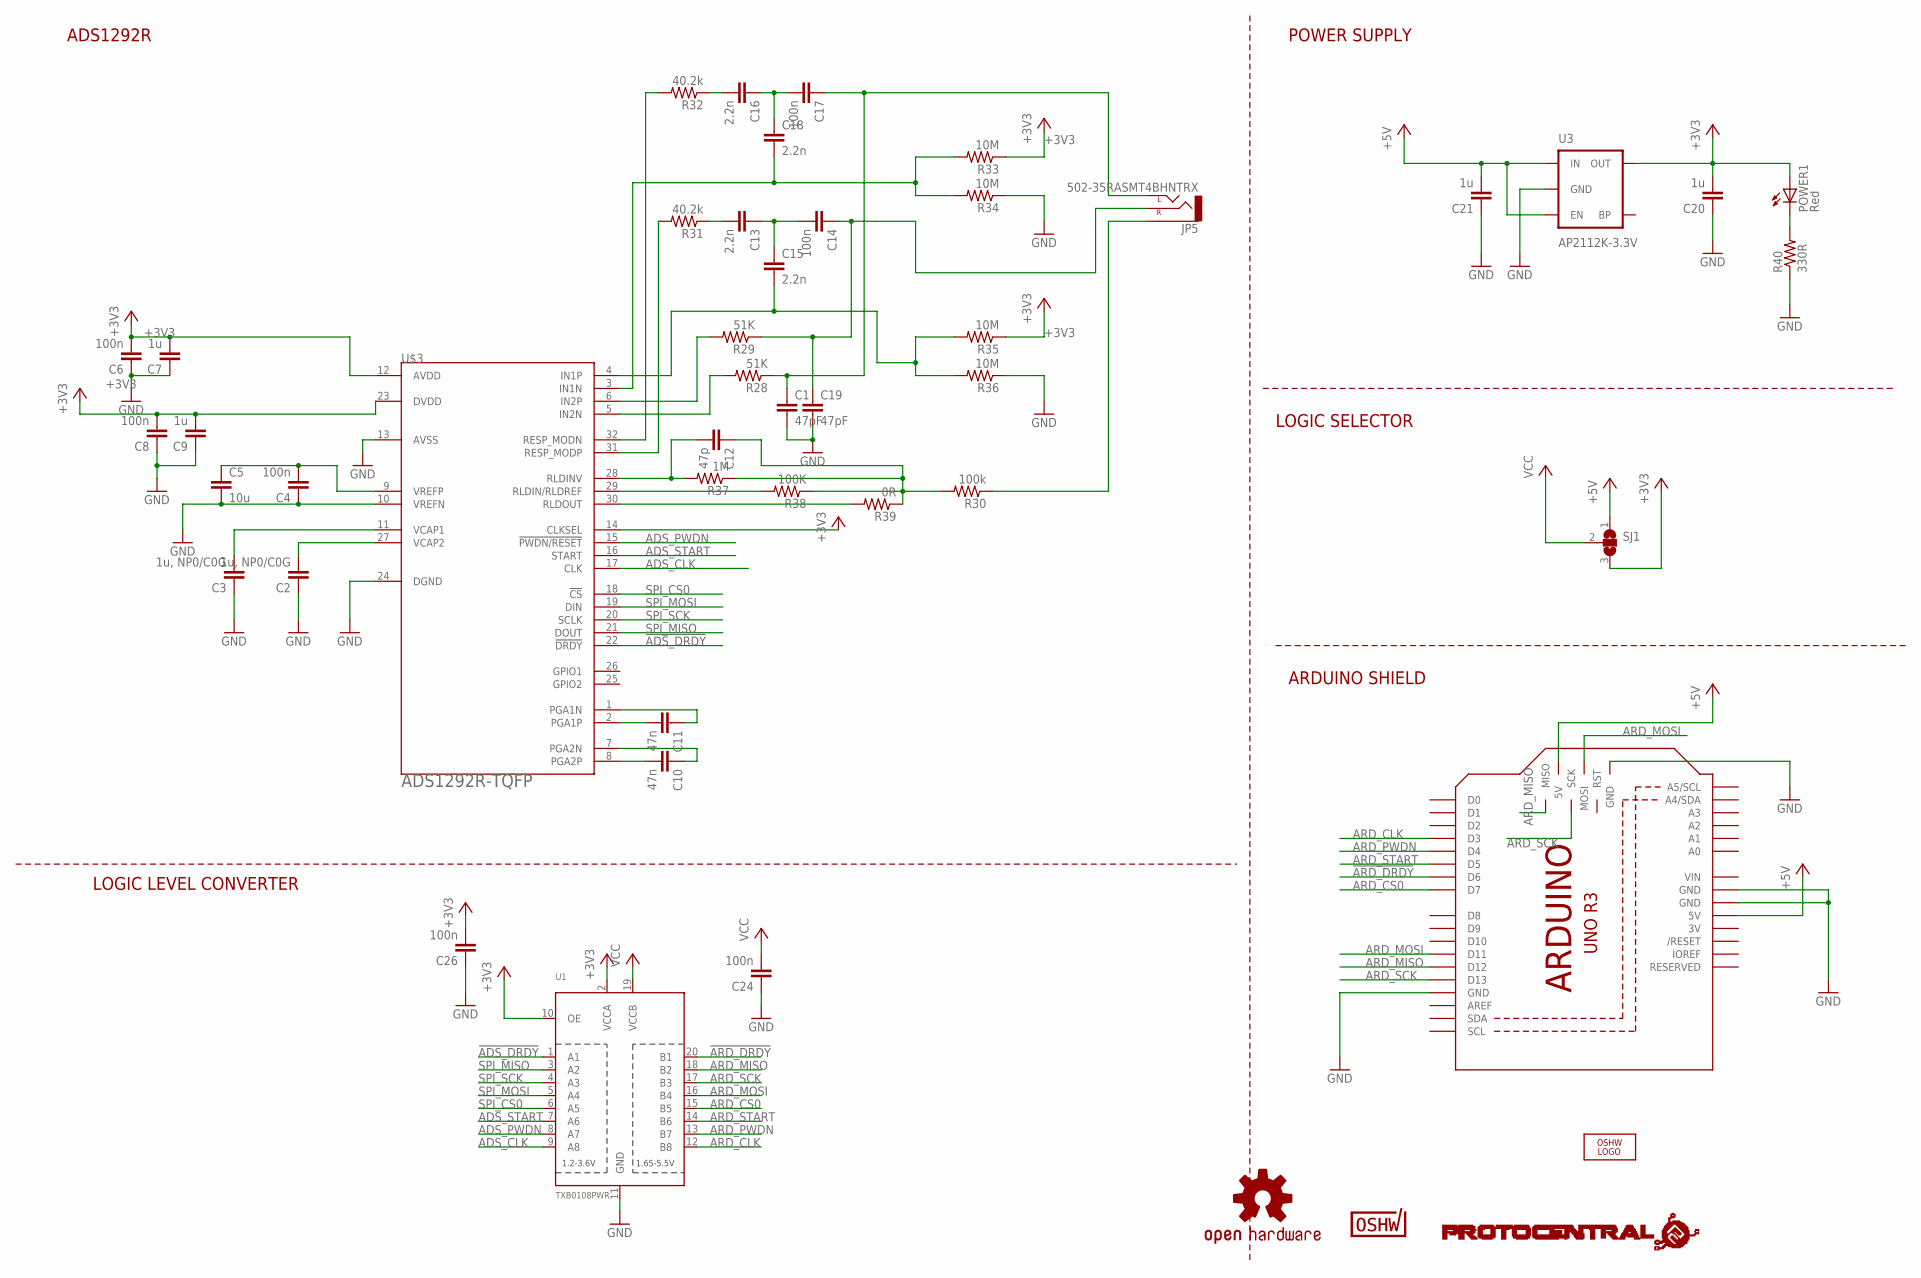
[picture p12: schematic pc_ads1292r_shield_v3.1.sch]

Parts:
C1, C19: 47pF; C0402
C2, C3: 1u, NP0/C0G; C0402
C4, C6, C8, C14, C17, C24, C26: 100n; C0402
C5: 10u; C0603
C7, C9, C20, C21: 1u; C0402
C10, C11: 47n; C0402
C12: 47p; C0402
C13, C15, C16, C18: 2.2n; C0402
JP5: 502-35RASMT4BHNTRX; AUDIO-JACK-3.5MM-SMD
LOGO1: OSHW_LOGO_FILLX0100-NT; OSHW_FILLX100_NOTEXT
M1: ARDUINO
POWER1: Red; CHIPLED_0603
R28, R29: 51K; R0402
R30: 100k; R0402
R31, R32: 40.2k; R0402
R33, R34, R35, R36: 10M; R0402
R37: 1M; R0402
R38: 100K; R0402
R39: 0R; R0402
R40: 330R; R0402
SJ1: SJ2W; SJ_2
U1: TXB0108PWR; TSSOP20
U3: AP2112K-3.3V; SOT23-5
U$1: CERT-SMALL; CERT-SMALL-SILK
U$3: ADS1292R-TQFP; SQFP-S-5X5-32
U$4: PROTY_LOGO_WITH_TEXT; PROTY_WITH_TEXT
U$6: OSHW-LOGOS; OSHW-LOGO-S

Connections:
3V: M1.3V
!ADS_DRDY: U1.1 (A1), U$3.22 (!DRDY)
!ARD_DRDY: M1.D6, U1.20 (B1)
+3V3: C6.2, C7.2, C8.2, C9.2, C20.2, C26.2, POWER1.A, R33.1, R35.1, SJ1.3, U1.2 (VCCA), U1.10 (OE), U3.5 (OUT), U$3.12 (AVDD), U$3.14 (CLKSEL), U$3.23 (DVDD)
+5V: C21.2, M1.5V, M1.5V_ICSP (5V), SJ1.1, U3.1 (IN), U3.3 (EN)
ADS_CLK: U1.9 (A8), U$3.17 (CLK)
ADS_PWDN: U1.8 (A7), U$3.15 (!PWDN/RESET)
ADS_START: U1.7 (A6), U$3.16 (START)
ARD_CLK: M1.D3, U1.12 (B8)
ARD_CS0: M1.D7, U1.15 (B5)
ARD_MISO: M1.D12, M1.MISO, U1.18 (B2)
ARD_MOSI: M1.D11, M1.MOSI, U1.16 (B4)
ARD_PWDN: M1.D4, U1.13 (B7)
ARD_SCK: M1.D13, M1.SCK, U1.17 (B3)
ARD_START: M1.D5, U1.14 (B6)
GND: C1.2, C2.1, C3.1, C4.1, C5.2, C6.1, C7.1, C8.1, C9.1, C19.2, C20.1, C21.1, C24.1, C26.1, M1.GND, M1.GND@1 (GND), M1.GND@2 (GND), M1.GND@3 (GND), R34.1, R36.1, R40.1, U1.11 (GND), U3.2 (GND), U$3.10 (VREFN), U$3.13 (AVSS), U$3.24 (DGND)
unnamed: C2.2, U$3.27 (VCAP2)
unnamed: C3.2, U$3.11 (VCAP1)
unnamed: C4.2, C5.1, U$3.9 (VREFP)
unnamed: C10.2, U$3.8 (PGA2P)
unnamed: C10.1, U$3.7 (PGA2N)
unnamed: C11.2, U$3.2 (PGA1P)
unnamed: C11.1, U$3.1 (PGA1N)
unnamed: C14.1, C19.1, JP5.RING (RIGHT), R29.1
unnamed: R39.2, U$3.30 (RLDOUT)
unnamed: JP5.SLEEVE, R30.1
unnamed: R31.2, U$3.31 (RESP_MODP)
unnamed: C13.2, R31.1
unnamed: C13.1, C14.2, C15.1
unnamed: R32.2, U$3.32 (RESP_MODN)
unnamed: C16.2, R32.1
unnamed: C16.1, C17.2, C18.1
unnamed: C1.1, C17.1, JP5.TIP (LEFT), R28.1
unnamed: C18.2, R33.2, R34.2, U$3.3 (IN1N)
unnamed: C15.2, R35.2, R36.2, U$3.4 (IN1P)
unnamed: R29.2, U$3.6 (IN2P)
unnamed: R28.2, U$3.5 (IN2N)
unnamed: C12.2, R37.2, U$3.28 (RLDINV)
unnamed: R38.2, U$3.29 (RLDIN/RLDREF)
unnamed: C12.1, R30.2, R37.1, R38.1, R39.1
unnamed: POWER1.C, R40.2
SPI_CS0: U1.6 (A5), U$3.18 (!CS)
SPI_MISO: U1.3 (A2), U$3.21 (DOUT)
SPI_MOSI: U1.5 (A4), U$3.19 (DIN)
SPI_SCK: U1.4 (A3), U$3.20 (SCLK)
VCC: C24.2, SJ1.2, U1.19 (VCCB)
VIN: M1.VIN

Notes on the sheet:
POWER SUPPLY
LOGIC SELECTOR
ARDUINO SHIELD
LOGIC LEVEL CONVERTER
ADS1292R

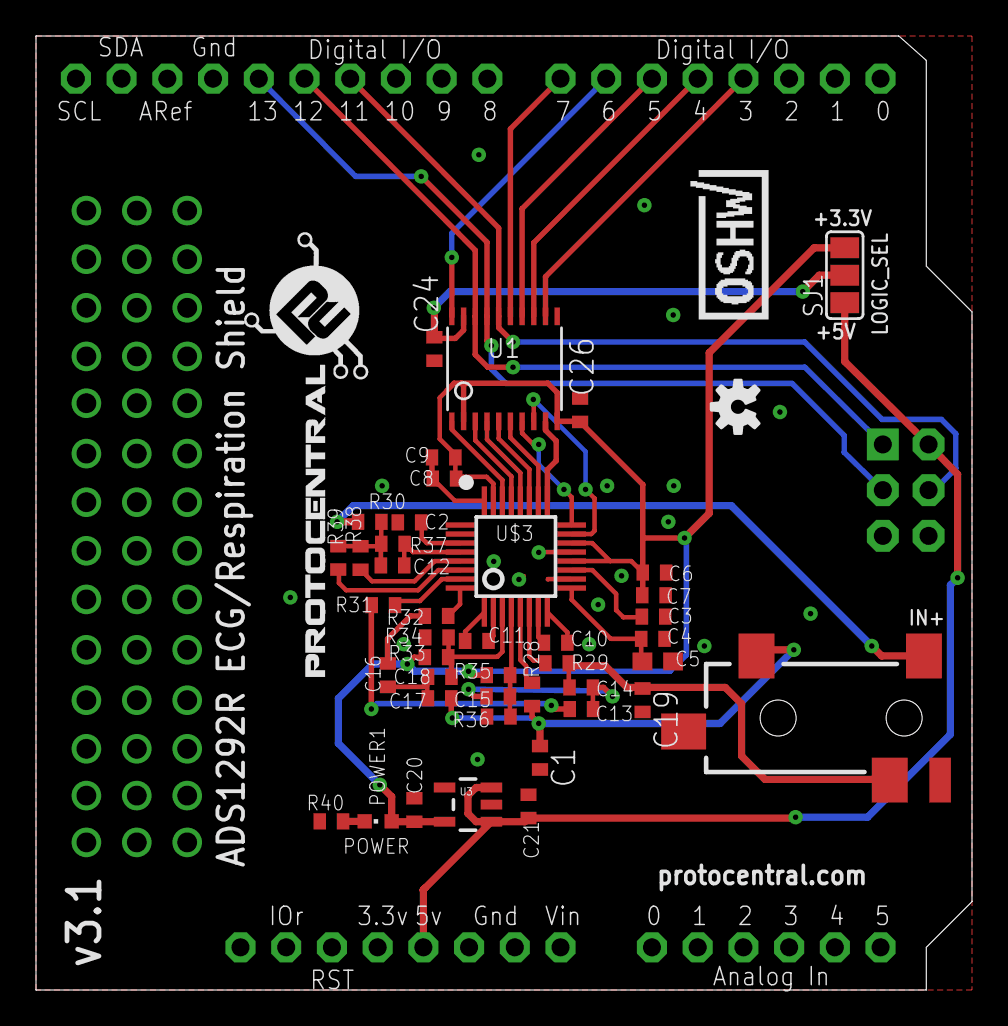
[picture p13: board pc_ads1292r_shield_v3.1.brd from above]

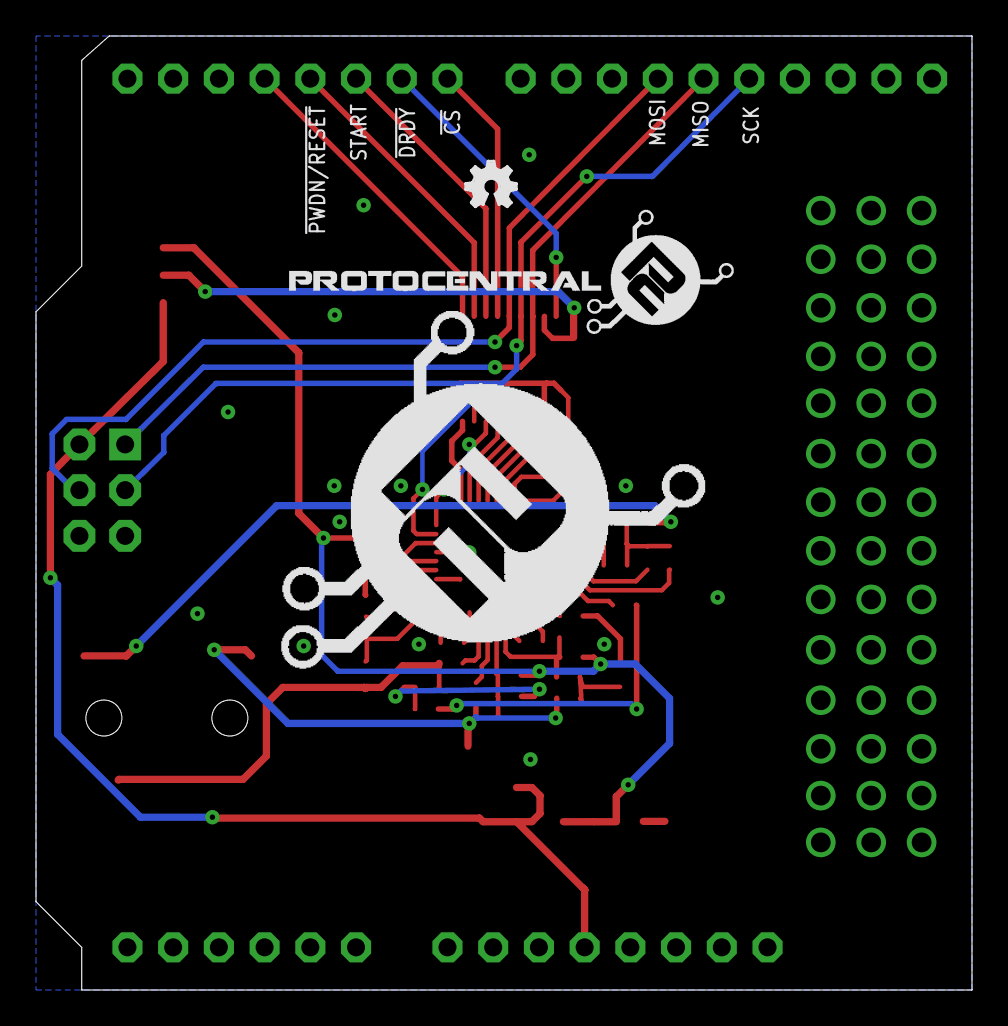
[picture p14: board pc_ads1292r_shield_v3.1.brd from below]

Board: 4 copper layers, 52.0 x 53.0 mm, 49 parts (3 on the bottom side), 45 nets.

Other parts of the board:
U$2: PROTY-LOGO-LARGE
U$5: PROTY_WITH_TEXT

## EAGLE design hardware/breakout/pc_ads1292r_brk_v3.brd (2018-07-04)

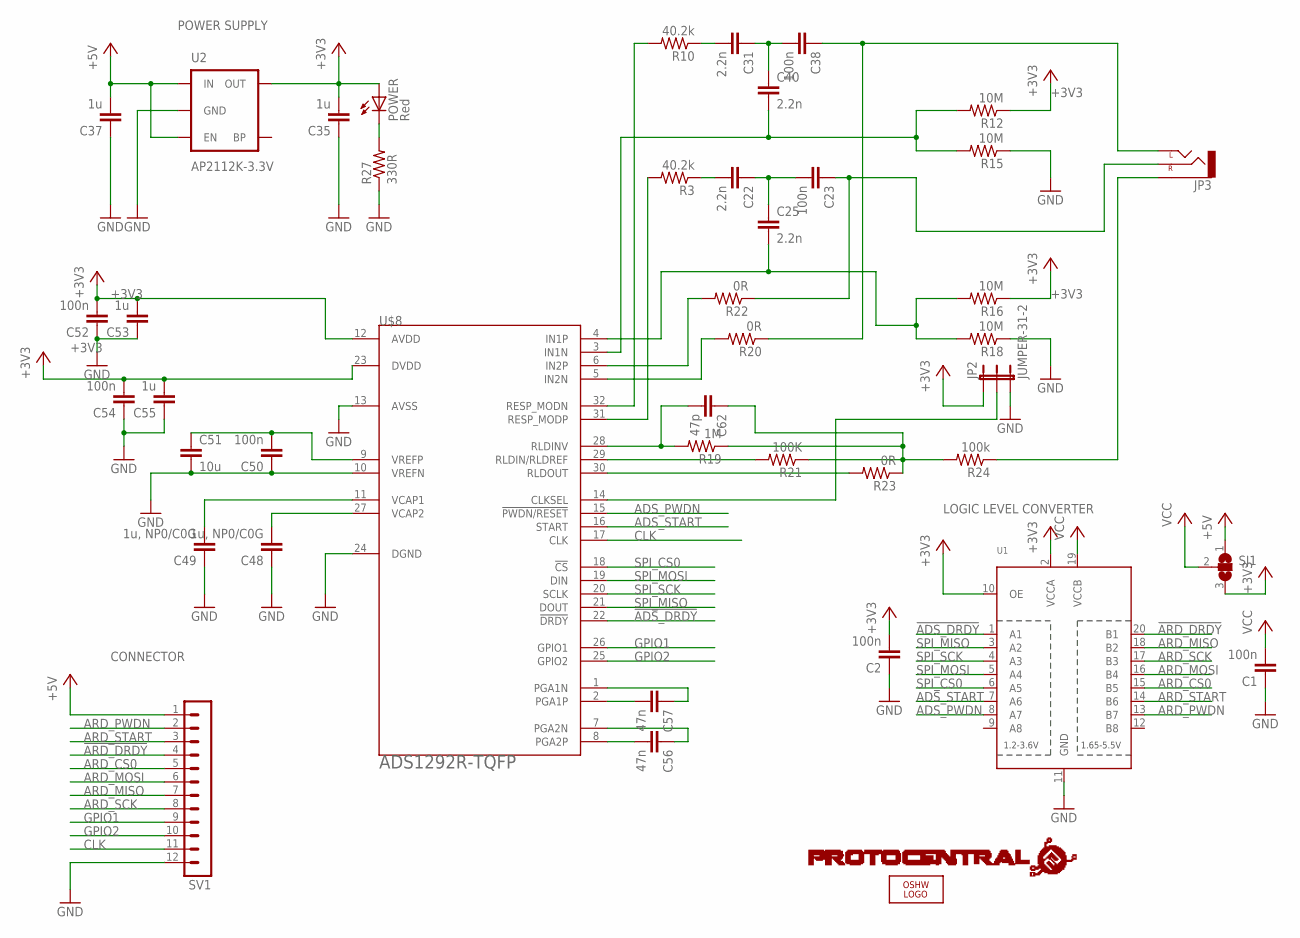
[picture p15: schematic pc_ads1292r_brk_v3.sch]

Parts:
C1, C2, C23, C38, C50, C52, C54: 100n; C0402
C22, C25, C31, C40: 2.2n; C0402
C35, C37, C53, C55: 1u; C0402
C48, C49: 1u, NP0/C0G; C0402
C51: 10u; C0603
C56, C57: 47n; C0402
C62: 47p; C0402
JP2: JUMPER-31-2; SJ_3_PASTE1&2
JP3: AUDIO-JACKSMD2; AUDIO-JACK-3.5MM-SMD
LOGO1: OSHW_LOGO_FILLX0100-NT; OSHW_FILLX100_NOTEXT
POWER: Red; CHIPLED_0603
R3, R10: 40.2k; R0402
R12, R15, R16, R18: 10M; R0402
R19: 1M; R0402
R20, R22, R23: 0R; R0402
R21: 100K; R0402
R24: 100k; R0402
R27: 330R; R0402
SJ1: SJ2W; SJ_2
SV1: MA12-1
U1: TXB0108PWR; TSSOP20
U2: AP2112K-3.3V; SOT23-5
U$1: PROTY-LOGO; LOGO-PROTY
U$8: ADS1292R-TQFP; SQFP-S-5X5-32

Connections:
!ADS_DRDY: U1.1 (A1), U$8.22 (!DRDY)
!ARD_DRDY: SV1.4, U1.20 (B1)
+3V3: C2.2, C35.2, C52.2, C53.2, C54.2, C55.2, JP2.1, POWER.A, R12.1, R16.1, SJ1.3, U1.2 (VCCA), U1.10 (OE), U2.5 (OUT), U$8.12 (AVDD), U$8.23 (DVDD)
+5V: C37.2, SJ1.1, SV1.1, U2.1 (IN), U2.3 (EN)
ADS_PWDN: U1.8 (A7), U$8.15 (!PWDN/RESET)
ADS_START: U1.7 (A6), U$8.16 (START)
ARD_CS0: SV1.5, U1.15 (B5)
ARD_MISO: SV1.7, U1.18 (B2)
ARD_MOSI: SV1.6, U1.16 (B4)
ARD_PWDN: SV1.2, U1.13 (B7)
ARD_SCK: SV1.8, U1.17 (B3)
ARD_START: SV1.3, U1.14 (B6)
CLK: SV1.11, U$8.17 (CLK)
GND: C1.1, C2.1, C35.1, C37.1, C48.1, C49.1, C50.1, C51.2, C52.1, C53.1, C54.1, C55.1, JP2.3, R15.1, R18.1, R27.1, SV1.12, U1.11 (GND), U2.2 (GND), U$8.10 (VREFN), U$8.13 (AVSS), U$8.24 (DGND)
GPIO1: SV1.9, U$8.26 (GPIO1)
GPIO2: SV1.10, U$8.25 (GPIO2)
unnamed: POWER.C, R27.2
unnamed: R3.2, U$8.31 (RESP_MODP)
unnamed: C22.2, R3.1
unnamed: C22.1, C23.2, C25.1
unnamed: R22.2, U$8.6 (IN2P)
unnamed: R20.2, U$8.5 (IN2N)
unnamed: C48.2, U$8.27 (VCAP2)
unnamed: R10.2, U$8.32 (RESP_MODN)
unnamed: C31.2, R10.1
unnamed: C31.1, C38.2, C40.1
unnamed: C38.1, JP3.TIP (LEFT), R20.1
unnamed: C40.2, R12.2, R15.2, U$8.3 (IN1N)
unnamed: C25.2, R16.2, R18.2, U$8.4 (IN1P)
unnamed: R21.2, U$8.29 (RLDIN/RLDREF)
unnamed: C62.2, R19.2, U$8.28 (RLDINV)
unnamed: C62.1, R19.1, R21.1, R23.1, R24.2
unnamed: C49.2, U$8.11 (VCAP1)
unnamed: C56.2, U$8.8 (PGA2P)
unnamed: C56.1, U$8.7 (PGA2N)
unnamed: C50.2, C51.1, U$8.9 (VREFP)
unnamed: C57.2, U$8.2 (PGA1P)
unnamed: C57.1, U$8.1 (PGA1N)
unnamed: C23.1, JP3.RING (RIGHT), R22.1
unnamed: R23.2, U$8.30 (RLDOUT)
unnamed: JP3.SLEEVE, R24.1
unnamed: JP2.2, U$8.14 (CLKSEL)
SPI_CS0: U1.6 (A5), U$8.18 (!CS)
SPI_MISO: U1.3 (A2), U$8.21 (DOUT)
SPI_MOSI: U1.5 (A4), U$8.19 (DIN)
SPI_SCK: U1.4 (A3), U$8.20 (SCLK)
VCC: C1.2, SJ1.2, U1.19 (VCCB)

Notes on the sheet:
LOGIC LEVEL CONVERTER
CONNECTOR
POWER SUPPLY

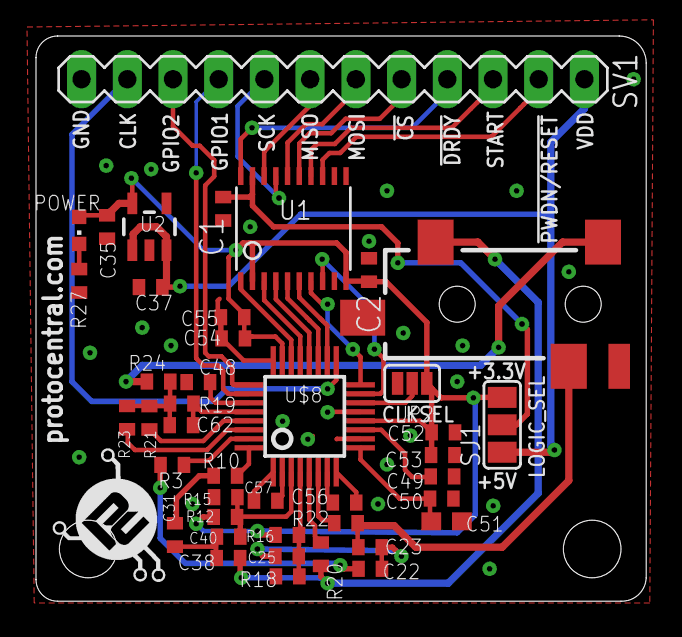
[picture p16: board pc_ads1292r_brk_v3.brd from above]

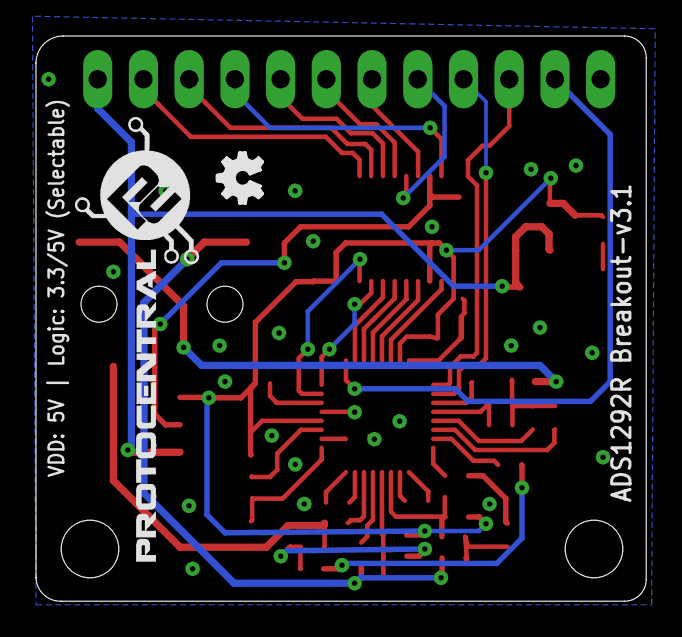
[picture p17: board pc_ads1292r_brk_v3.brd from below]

Board: 4 copper layers, 33.9 x 31.4 mm, 45 parts (2 on the bottom side), 47 nets.

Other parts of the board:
U$2: PROTY_WITH_TEXT

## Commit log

2015-10-22 Design File
    [pc_ads1292r_brk.brd, pc_ads1292r_brk.sch, pc_ads1292r_shield_v2.brd, pc_ads1292r_shield_v2.sch]
2016-06-15 added arduino processing sketch
2016-08-23 Added processing sketch for Arduino
2016-10-14 Arduino Library
2016-12-01 added new design file
    [pc_ads1292r_brk_v3.brd, pc_ads1292r_brk_v3.sch]
2017-08-22 Added Heart rate algorithm
    Added filter function, Heart rate calculation.
2020-12-31 Removed existing GUI and Arduino library (moved)
2020-12-31 Renamed hardware folder
    [pc_ads1292r_brk_v3.brd, pc_ads1292r_brk_v3.sch, pc_ads1292r_shield_v3.1.brd, pc_ads1292r_shield_v3.1.sch]

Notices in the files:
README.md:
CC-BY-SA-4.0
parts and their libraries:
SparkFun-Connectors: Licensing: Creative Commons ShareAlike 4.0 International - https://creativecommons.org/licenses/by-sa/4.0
